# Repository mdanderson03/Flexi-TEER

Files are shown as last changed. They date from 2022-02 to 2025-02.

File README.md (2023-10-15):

# 






## What is Flexi-TEER

Flexi-TEER is an adaptable, powerful open-source transepitheal electrical resistance measurement device. Such tool is used by scientists who want to estimate the thickness of the layer of cells in a non-distructive way.

**T**rans**E**pithelial **E**lectrical **R**esistance (TEER) is an electrophysiology technique where resistance across a cell layer is measured as a proxy for ion flow which is related to inter-cellular tight junction formation.

## Where we are

At the moment the project is at the stage of hardware testing and software development. The testing status can be tracked in [this document](/Electronics/6_BringUp/FlexiTeer_BringUp_report.odt).
We recommend using OnlyOffice for the table of contents to work correctly.

Photo of the prototype

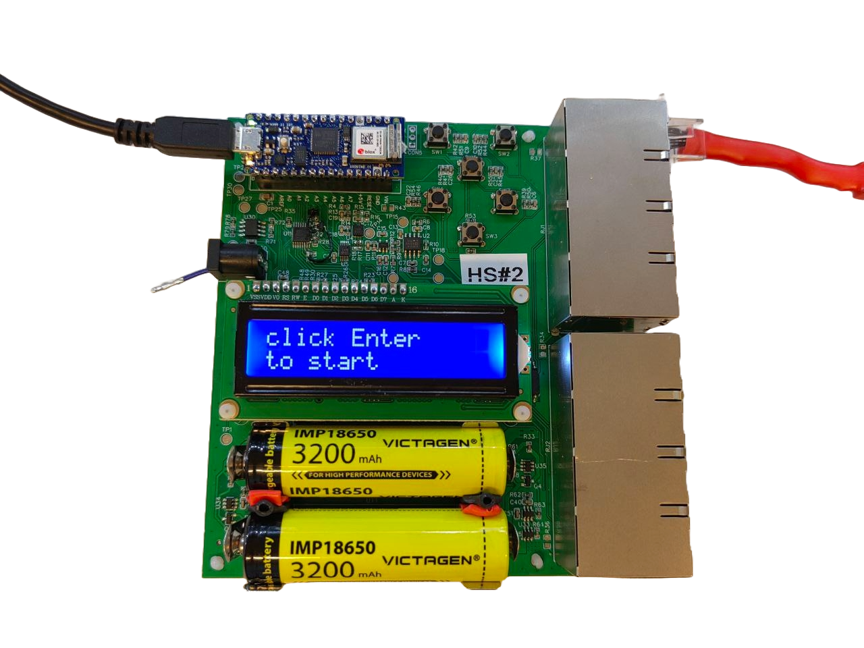
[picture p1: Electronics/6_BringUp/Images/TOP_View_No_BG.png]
TOP_View


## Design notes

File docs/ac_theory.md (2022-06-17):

# AC Theory

The DC analysis section is interesting, but not practical. The charge build up on membranes is a health hazard to the cells and it still depends on measuring within a time window. Too fast and charge has not sufficiently built
up on the cells membrane to force all of the current through the tight junctions. Too slow and and the current can become too low to accurately measure. 

To address these concerns and to extract more components, we turn to AC analysis.

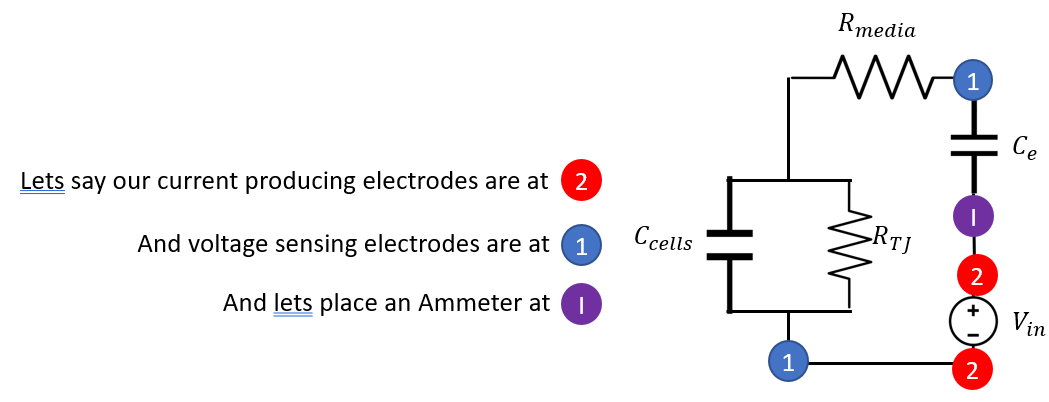
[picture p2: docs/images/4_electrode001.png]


We are still using the 4 electrode circuit, but we just use AC current instead of DC.

```math
\tag{1} Z = Z_{1}+Z_{2}
```

```math
\tag{2} Z_{1}=R_{med}+ \dfrac{-j}{\omega*C_{e}}
```

Where -j is imaginary i (standard syntax for electronics as i is typically a current value) and omega is angular freq. 

```math 
\tag{3} Z_{2}= \dfrac{1}{\dfrac{1}{R_{TJ}}+j*\omega*C_{cells}}=\dfrac{R_{TJ}}{1+j*\omega*C_{cells}*R_{TJ}}
```

Multiple (3) by the complex conjugate of its denominator

```math
Z_{2}= \dfrac{R_{TJ}*(1-j*\omega*C_{cells}*R_{TJ})}{1+\omega^2*C_{cells}^2*R_{TJ}^2}= [\dfrac{1}{1+\omega^2*C_{cells}^2*R_{TJ}^2}]*(R_{TJ}-j*\omega*C_{cells}*R_{TJ}^2)
```

Separate terms that are real and imaginary

```math
Z = [\dfrac{1}{1+\omega^2*C_{cells}^2*R_{TJ}^2}]*[(R_{TJ}+R_{med}+\omega^2*C_{cells}^2*R_{TJ}^2)+ j*[(-\omega^2*C_{e}*C_{cells}*R_{TJ}^2-1-\omega^2*C_{cells}^2*R_{TJ}^2)*\dfrac{1}{\omega*C_{e}}]]
```

Lets make some new variables to make it easier to read

```math
\tag{6} \alpha = \dfrac{1}{1+\omega^2*C_{cells}^2*R_{TJ}^2}, \quad \beta = \dfrac{1}{\omega*C_{e}}
```

Sub (6) into (5)

```math
Z = \alpha*[(R_{TJ}+R_{med}+\omega^2*C_{cells}^2*R_{TJ}^2) +j*\beta*[-\omega^2*C_{e}*C_{cells}*R_{TJ}^2-\omega^2*C_{cells}^2*R_{TJ}^2-1]]
```

Lets reduce this further

```math
R_{base}= R_{TJ}+R_{med}+\omega^2*C_{cells}^2*R_{TJ}^2, \quad and \quad X_{base} =-(\omega^2*C_{e}*C_{cells}*R_{TJ}^2+\omega^2*C_{cells}^2*R_{TJ}^2+1)
```

```math
\tag{7} Z = \alpha*[R_{base} -j*\beta*X_{base}]
```

Next to find the total resitance we must find the complex magnitude to solve for it. 

```math
\tag{8} \mid Z \mid = \sqrt[2]*{z*z^{\star}}= \alpha*\sqrt[2]*{R_{base}^2+\beta^2*X_{base}}
```

Lets look at some cases. The first will be high frequency.

```math
\tag{9} if \quad w \gg 1, \beta*X_{base} \approx \dfrac{\omega^2}{\omega*C_{e}} (C_{e}*C_{cells}*R_{TJ}^2+C_{cells}^2*R_{TJ}^2) \propto \omega
```

```math
\tag{10} R_{base} \approx \omega^2*C_{cells}^2*R_{TJ}^2*R_{media} \propto \omega^2 
```

R_base contributes to a higher degree than X_base and thus

```math
\tag{11} Z \approx \alpha*\omega^2*C_{cells}^2*R_{TJ}^2 \approx \dfrac{\omega^2*C_{cells}^2*R_{TJ}^2*R_{media}}{\omega^2*C_{cells}^2*R_{TJ}^2}=R_{media}
```

Now lets turn to the opposite end of the spectrum and find the solution at small omegas

```math
\tag{12} at \quad \omega \ll 1, \quad  X_{base} \approx 1 , \quad R_{base} \approx R_{TJ} +R_{media}
```

and

```math
\tag{13} \alpha \approx 1, \quad \beta = \dfrac{1}{\omega*C_{e}}
```

thus

```math
\tag{14} Z \approx \sqrt[2]*{(R_{TJ} +R_{media})^2 + \dfrac{1}*{\omega*C_{e}}^2} \approx \dfrac{1}{\omega*C_{e}}
```

In summary

```math
\tag{15} if \quad \color{blue}{\omega \gg 1, \quad Z \approx R_{media}} \color{black} \quad and \quad at \quad \color{red}{\omega \ll 1, \quad Z \approx \dfrac{1}{\omega*C_{e}}}
```

This allows us to perform something called impedence spectroscopy. At low freq we can determine the electrode capacitance and at high freq we can determine the resistance in the media. Subbinng those terms in and doing
a regression to the full solution allows us to determine the cell capacitance and tight junctional resistance. Notice too in this method that nothing was time depended and thus no integrals to perform over hard to determine variables.
Below is a sample spectra of impedences from the full solution.

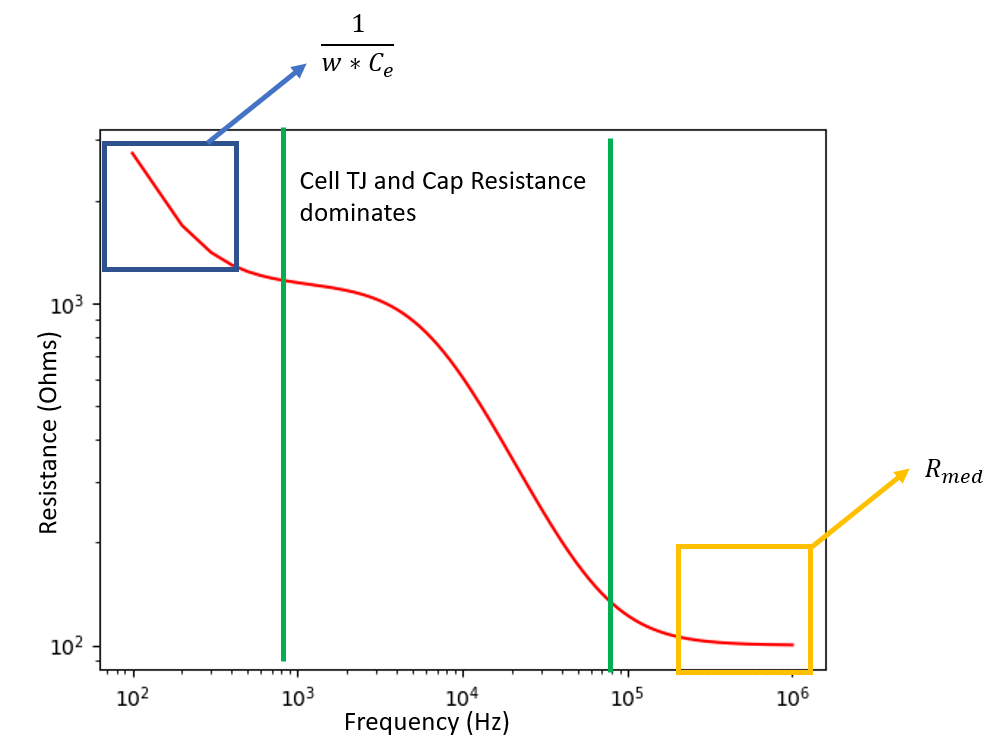
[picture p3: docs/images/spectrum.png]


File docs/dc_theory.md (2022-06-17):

# DC Theory

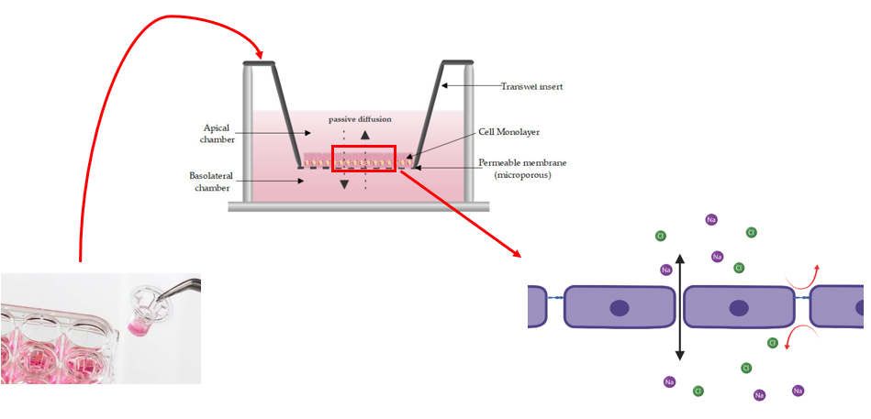
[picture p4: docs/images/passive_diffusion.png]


The typical use of TEER is with transwells. In these, monolayers of cells are formed and ions can passively diffuse through the gaps between cells.

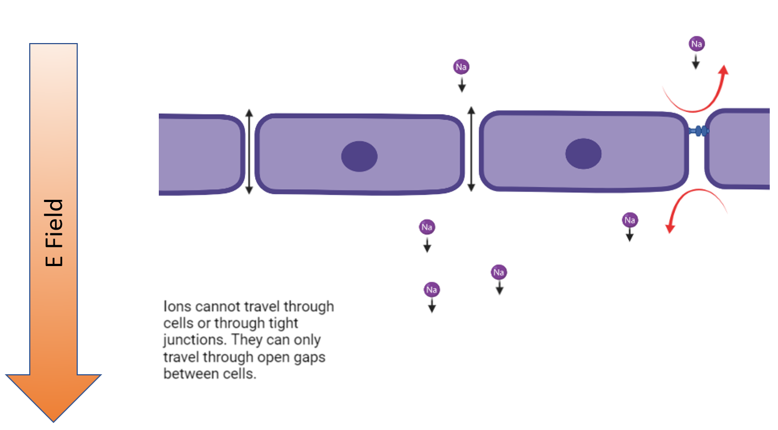
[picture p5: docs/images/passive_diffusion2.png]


Lets start forming a model on this. So if a gap has a tight junction formed, it blocks the ion from going through it. If it lacks a tight junction, then the ion can go on through. Lets translate that into a simple electrical circuit model.

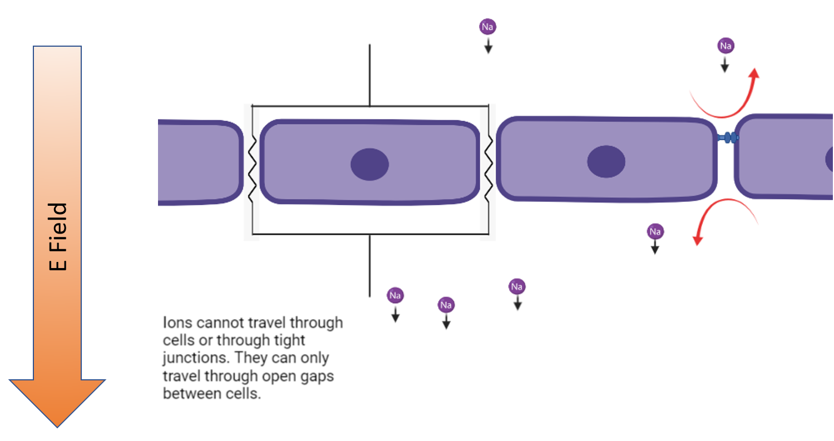
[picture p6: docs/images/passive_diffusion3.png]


So we replace tight junctions and cells with open circuits and given gaps restrict the rate that charged particles can pass through the monolayer, lets say they are  resistors. So **tight junctions and cells = open circuit** and **gaps = resistors**

**Ohm's Law**
```math
 \tag{1} V = I*R 
```

**Parallel Resistance Equivalency**
```math 
 \tag{2} R_{eq} = \dfrac{1}{(\sum{\dfrac{1}{R_g}})}
```

All gap resistances are approximately equal

```math 
  \tag{3} R_{1} \approx R_{2} \approx R_{3} \approx ... \approx R_{G}
```

Sub [3] into [2]

```math 
 \tag{4} R_{eq} = \dfrac{1}{(\dfrac{1}{R_G}*N_{G})}=\dfrac{R_{G}}{N_{G}}
```

```math 
 \tag{5} N_{CJ}=N_{TJ}+N_{G} \to N_{G} = N_{CJ}-N_{TJ}
```

Sub (3) into (4) and taylor expand 

```math 
 \tag{6} R_{eq}=\dfrac{R_{G}}{N_{CJ}*(1-\dfrac{ N_{TJ}} {N_{CJ}})} \to \dfrac{R_{eq}*N_{CJ}}{R_{G}} = \dfrac{1}{(1-\dfrac{N_{TJ}}{N_{CJ}})} \approx 1+ \dfrac{N_{TJ}}{N_{CJ}}
```

Thus

```math 
 \tag{7} R_{eq} \propto N_{TJ}
```

In the previous model we considered cell bodies themselves as open circuits, but is that accurate? Check out the image below to see that they are more accurately capacitors!

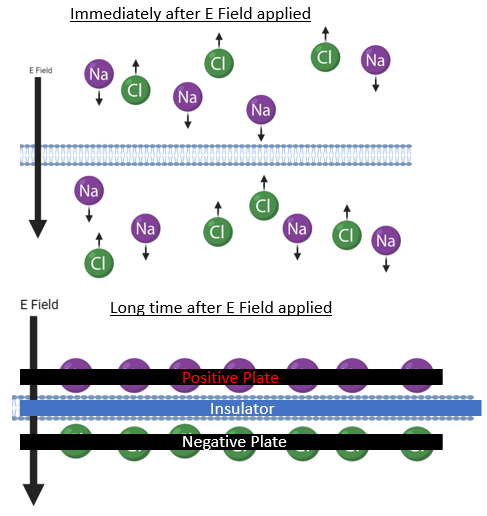
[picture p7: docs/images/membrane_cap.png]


Now lets add the cell capacitance and resistance due to the media into the model circuit

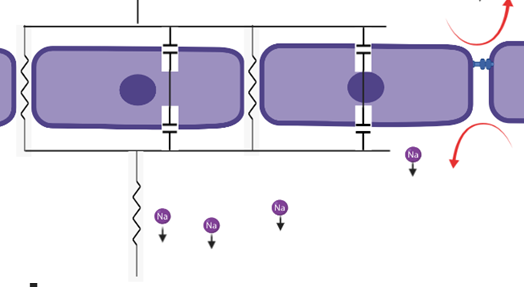
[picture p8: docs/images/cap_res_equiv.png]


We need Kirchoff Loop and Node Equations to solve this one:

```math 
 \tag{8} \color{blue}{V_{in}-R_{media}*I -R_{TJ}*I_{TJ}=0}
```

```math 
 \tag{9} \color{red}{V_{in}-R_{media}*I-V_{cells}=V_{in}-R_{media}*I-\dfrac{Q}{C_{cells}}=0}
```

```math 
 \tag{10} \color{yellow}{I=I_{TJ}+I_{cells}}
```

The node and loops look like this (color coordinated)

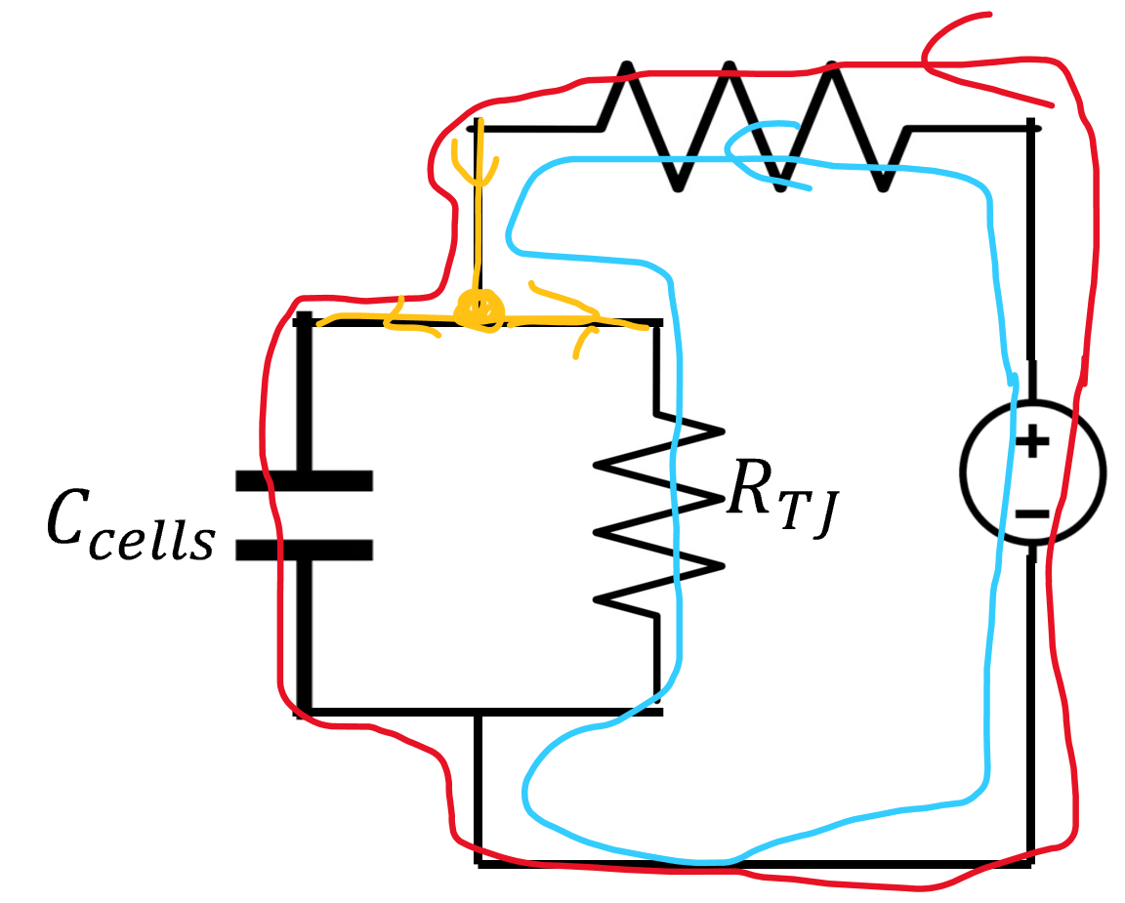
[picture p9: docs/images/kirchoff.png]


Set (8) equal to (9)

```math 
 \tag{11} \dfrac{Q}{C_{cells}}=R_{TJ}*I_{TJ}\to \color{red}{I_{TJ}=\dfrac{Q}{R_{TJ}*C_{cells}}}
```

Sub (11) into (10)

```math 
 \tag{12} I = \dfrac{Q}{R_{TJ}*C_{cells}} + I_{cells}
```

Sub (12) into (9)

```math 
 \tag{13} V_{in}-R_{media}*(\dfrac{Q}{R_{TJ}*C_{cells}}+I_{cells})-\dfrac{Q}{C_{cells}}=0
```

Divide by R media

```math 
 \tag{14} \dfrac{V_{in}}{R_{media}}-I_{cells}-(\dfrac{1}{R_{TJ}*C_{cells}}-\dfrac{1}{R_{media}*C_{cells}})*Q=0
```

Place I and Q onto opposite sides of equation

```math 
 \tag{14} -R_{media}*C_{cells}*I_{cells}=(\dfrac{R_{media}}{R_{TJ}}+1)*Q-C_{cells}*V_{in}
```

Given Q is built up on the membranes, the whole current that passes through cells is the time derivative of the charge and lets group some constants into a new constant

```math 
 \tag{16} I_{cells}=\dfrac{\delta{Q}}{\delta{t}}, \alpha = \dfrac{R_{media}}{R_{TJ}} + 1
```

Sub (16) into (15)

```math 
 \tag{17} -R_{media}*C_{cells}*\dfrac{\delta{Q}}{\delta{t}}=\alpha*Q-C_{cells}*V_{in}
```

Separate Q and t terms to opposite sides of equation

```math 
 \tag{18} \dfrac{\delta{Q}}{Q-\dfrac{V_{in}*C_{cells}}{\alpha}}=\dfrac{-\alpha}{C_{cells}*R_{media}}*\delta{t}
```

Integrate (18)

```math 
 \tag{19} \int_{0}^{Q}  \dfrac{1}{Q-\dfrac{V_{in}*C_{cells}}{\alpha}}\delta{Q}=\int_{0}^{t} \dfrac{-\alpha}{C_{cells}*R_{media}}\delta{t}
```

Solution to (19)
```math 
 \tag{20} \ln{\dfrac{Q-\dfrac{V_{in}*C_{cells}}{\alpha}}{\dfrac{-V_{in}*C_{cells}}{\alpha}}}=\dfrac{-\alpha*t}{C_{cells}*R_{media}}
```

Raise each side to power e and solve for Q

```math 
 \tag{21} \color{red} Q(t)=\dfrac{V_{in}*C_{cells}}{\alpha}*(1-e^{\dfrac{-\alpha*t}{C_{cells}*R_{media}}})
```

now lets solve for I and V for cells (time derivative of Q and Q/C respectively)

```math 
 \tag{22} \color{red} I_{cells}(t)=\dfrac{V_{in}}{R_{media}}*e^{\dfrac{-\alpha*t}{C_{cells}*R_{media}}}
```
```math 
 \tag{23}  \color{red} V_{cells}(t)= \dfrac{V_{in}}{\alpha}*(1-e^{\dfrac{-\alpha*t}{C_{cells}*R_{media}}})
```

Now lets insert a volt and an am meter into the circuit

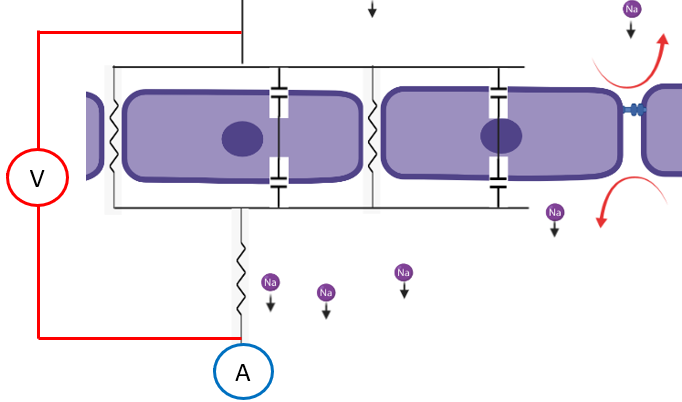
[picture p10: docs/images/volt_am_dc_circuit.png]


```math 
 \tag{24} V_{meter}(t)=R_{TJ}*I_{TJ}(t)+R_{media}*I(t)
```

```math 
 \tag{25} Blank = R_{media}*I(t)
```
```math 
 \tag{26} V_{meter}(t)-Blank=R_{TJ}*I_{TJ}(t)
```

```math 
 \tag{27} I_{meter}(t)=I(t)=I_{cells}+I_{TJ} \to I_{TJ}=I_{meter}(t)-I_{cells}
```

Sub (22) into (27)

```math 
 \tag{28} I_{TJ}(t)=I_{meter}(t)-\dfrac{V_{in}}{R_{media}}*e^{\dfrac{-\alpha*t}{C_{cells}*R_{media}}}
```

Sub (28) into (26) and solve for the tight junctional resistance

```math 
 \tag{29} \color{red}R_{TJ}=\dfrac{V_{meter}(t)-Blank}{I_{meter}(t)-\dfrac{V_{in}}{R_{media}}*e^{\dfrac{-\alpha*t}{C_{cells}*R_{media}}}}
```

So to solve for tight junctional resistance we must know how current has been applied to the circuit. That is a finicky to determine and beyond this we have a confounding factor of tight junction resistance being in the alpha term. To rectify this, lets drive this to inifinite time

```math 
 \tag{30} R_{TJ}(t)=\dfrac{V_{meter}(t)-Blank}{I_{meter}(t)}
```

This equation is easily solved with our instruments as long as we wait long enough. Lets take a stab at how fast that might be given I dont have infinite time to wait. Lets say we want to wait until the cell current has fallen to a factor of 0.01% of its original value

```math 
 \tag{31} 0.0001 =e^{\dfrac{-\alpha*t}{C_{cells}*R_{media}}}
```

```math 
 \tag{32} \ln{0.0001}=\dfrac{-\alpha*t}{C_{cells}*R_{media}}, \alpha \approx 1 \quad if \quad R_{TJ} \gg R_{media}
```

```math 
 \tag{33} -R_{media}*C_{cells}*\ln{0.0001}=t
```

To find cells we take the unit capacitance and multiply by transwell area

```math 
 \tag{34} C_{cells}=A_{transwell}*C_{unit}=3.3*10^{-5}*1*10^{-2}=3.3*10^{-7}, R_{media} \approx 50
```

```math 
 \tag{35} t = 3.3*10^{-7}*50*\ln{0.0001} \approx 0.1ms 
```

So saturation occurs very rapidly! We have another issue now. Its something that wasn't addressed in the previous model. Lets check out what happens to an electrode the second current flows from it. 

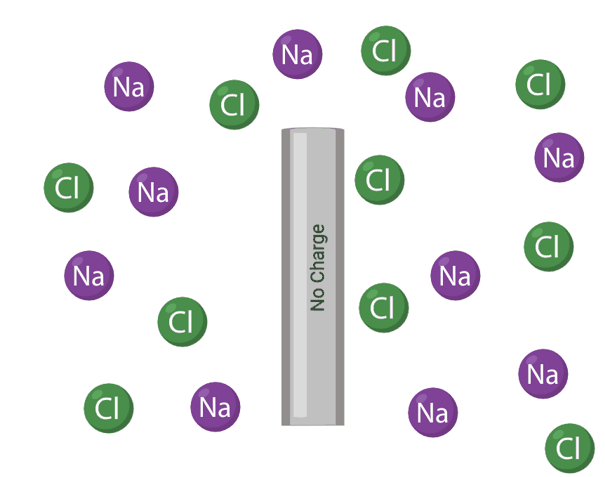
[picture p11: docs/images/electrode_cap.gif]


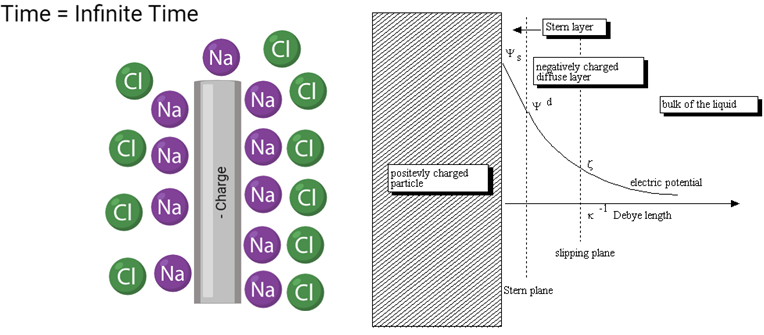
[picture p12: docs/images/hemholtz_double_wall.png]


  As can be seen, a double wall is created whenever an electrode generates current in a liquid with negative and positive ions in it. This creates another component called electrode capacitance that we must add into the circuit. Beyond this, thus far we have neglected to consider a trans-cellular transport component. Here is the new circuit.

.. image:: C:\Users/mike/Documents/GitHub/Felxi-TEER/images/teer_theory/el_cap_trans.png
  :width: 800

```math 
 \tag{36} R_{TJ}+R_{TC}=R_{cells}
```

Experiments can be made to emphasize the transcellular transport component, but in general

```math 
 \tag{37} R_{TJ} \gg R_{TC}
```

```math 
 \tag{38} R_{cells} \approx R_{TJ}
```

Instead of resolving the entire equation with electrode capacitence in it, lets think of them like a current squeeze. At t=0, its like a short circuit, at infinite time its like a closed circuit. We also know the general form of how the current will change over time. 

```math 
 \tag{39} R_{TJ}=\dfrac{V_{meter}(t)-Blank}{I_{meter}(t)-\dfrac{V_{in}}{R_{media}}*e^{\dfrac{-\alpha*t}{C_{cells}*R_{media}}}}* \color{red} \dfrac{1}{e^{\dfrac{-\beta*t}{C_{e}*R_{media}*R_{TJ}}}}
```

I dont really care what beta actually is. This is the correct form and that is all that is needed for this approximation. Lets see where this equation goes as t goes to infinity

```math 
 \tag{40} as \quad t \to \infty, \quad R_{TJ} \to \infty
```

This is nonsense, right? tight junctional resistance is constant, but what happened? In this model we assumed that all voltage dropped occured over media and the tight junctions. Now we are getting a drop over the electrode capcitance too. Lets substract that from (39) to get the proper equation.

```math 
 \tag{41} R_{TJ}=\dfrac{V_{meter}(t)-Blank- \color{red} V_{c}(t)}{I_{meter}(t)-\dfrac{V_{in}}{R_{media}}*e^{\dfrac{-\alpha*t}{C_{cells}*R_{media}}}}*\dfrac{1}{e^{\dfrac{-\beta*t}{C_{e}*R_{media}*R_{TJ}}}}
```

We have an issue though. The voltage drop over the electrode capacitance depends on time so we would need to solve the equation

```math 
 \tag{42} \int_{0}^{t}I_{electrode}dt = \int_{0}^{t}\dfrac{1}{e^{\dfrac{-\beta*t}{C_{e}*R_{media}*R_{TJ}}}}dt
```

That equation is difficult to solve accurately since it depends on us again knowing the exact time since the circuit was turned on. Is there a way to bypass this component though?



Up until now I was using the same electrodes to generate the current and read the voltage. If we make a new configuration where 2 separate voltage sensing electrodes are added and placed between the current electrodes and cell sample, we get a new configuration where the part of the circuit that the electrodes are measuring does not inlcude the electrode capcitor component, thus making it so we can revert make the original equation that never depended on the voltage drop over the electrode capacitor. Thus

```math 
 \tag{43} \color{red} R_{TJ}=\dfrac{V_{meter}(t)}{I_{meter}(t)} - R_{blank}
```

This still has a caveat where the electrode capacitance is still pinching current off. While my tight junctional resistance value does not care, at some point my current will become so small that my electronics cannot accurately measure it anymore. Now you may be asking well current still must go into the voltage electrodes right? In that case won't they get capacitence themselves and we will be back in the same same boat. This is true and capacitance is a geometrical term so our capacitence is the same (assuming the electrodes are identical in shapes), but there is one big thing here. 

```math 
 \tag{44} V=\dfrac{Q}{C}
```

The voltage drop is what really matters when we are measuring voltage differences, not the capcitence itself. If infinite time elapses we will be in the same boat, but in shorter time frames we are good. This is due to the current that the voltage electrodes flow is in the order of picoamps while the current electrodes make micro amps. This means the voltage drop over the voltage electrodes capacitence is much much lower at short time frames since the charge can only accumulate at a very low rate.

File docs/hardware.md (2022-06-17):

# Hardware

!The basic goal of this electronic device is to create a low fixed current, AC square wave with modulatable frequency and measure the voltage difference between the current electrodes. 

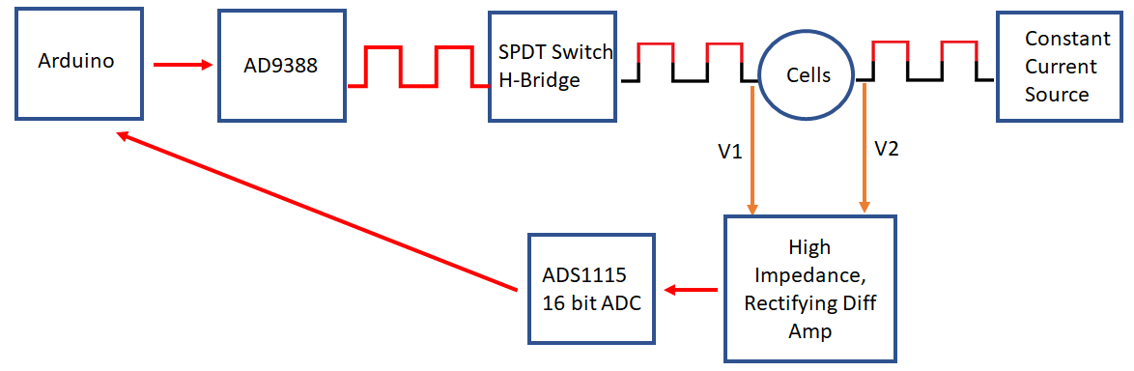
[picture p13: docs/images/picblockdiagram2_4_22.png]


Looking at the block diagram we can see that An Arduino was used as the microcontroller for the device. A AD9388 breakout board generates a square wave timing wave that goes between V and 0 volts. An H-Bridge made from single throw dual throw (SPDT) switches allows it to be made into an AC wave at the same freq, but between +-V Volts. A constant current chip forces the current in that AC wave to be locked into a small value (20uA). The voltage difference over the cells then goes into a high input impedance diff amp. Since the incoming signal is +-V_diff, it would generate an AC output which is then hard to read off. So inside that block are two more SPDT switches to flip what input what end goes to so that the high V is always in the same input which effectively makes the diff amp output a DC signal. This signal then goes into a 16bit ADC which can be read off onto the Arduino. 

All schematics and PCB design we performed on the EasyEDA website. Click here to be directed to the project on [EasyEDA](https://oshwlab.com/md.anderson03/flexi-teer)

Lets take a look at and explore the overall schematic:



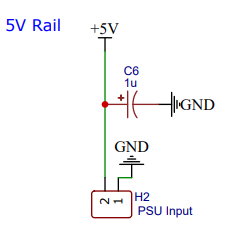
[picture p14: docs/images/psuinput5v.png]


Primary power supply is a 5V external supply which is filter by internal 1uF cap. 

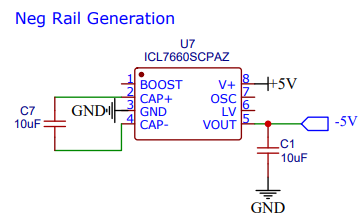
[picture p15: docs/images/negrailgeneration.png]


Use switching regulator chip to generate negative voltage rail which is needed for OP Amps in circuit to function properly. 

>!! **Warning**
>!! This part has been an issue. Gets very hot and tends to fail rapidly.

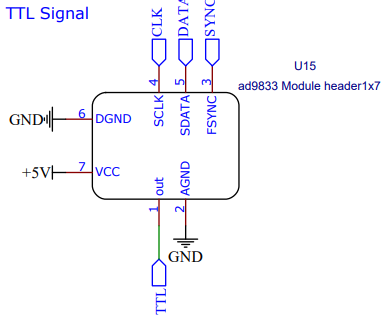
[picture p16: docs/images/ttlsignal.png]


The AD9388 chip is the effective "clock" for this device. It has a serial connection to the Arduino and can modulate its square wave output freq between single hertz and mega hertz. This provides the Arduino with a signal that triggers it to ask for a voltage read with (some delay/phase shift may be added to that in the Arduino itself). It also flips the output of all 6 SPDT switches. This allows them to generate an AC square wave allows them to flip polarity on the differential amp so that its output is DC like and positive. 

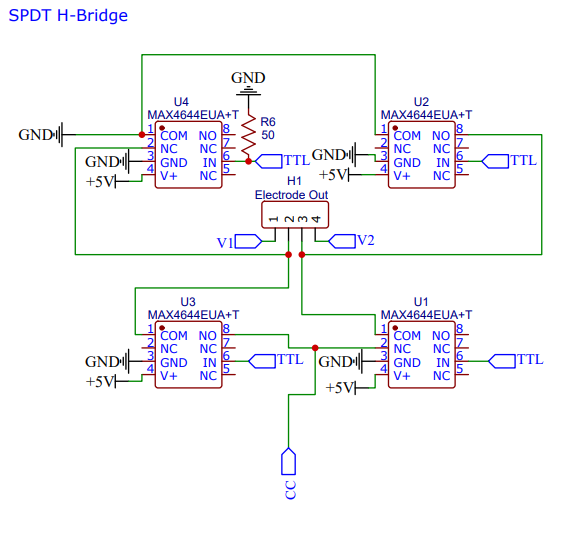
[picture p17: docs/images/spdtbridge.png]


This section converts the incoming TTL wave into an AC version. Its the exact same construction as a DC motor H-Bridge, but instead of bi-junctional transistors, it uses SPDT switches. This allows it to perform at MHz and have minimal artifacts. 

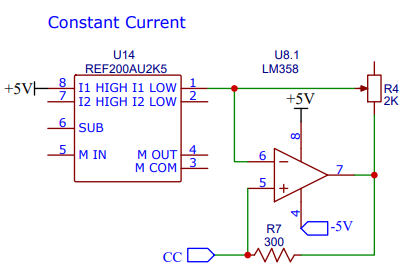
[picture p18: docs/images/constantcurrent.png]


This module needs a constant current source. The REFE200AU2K5 IC has a built in 100uA constant current source. The goal for this device was 20uA. To accomplish that a LM358 op amp was added to scale down the current. A potentiometer is installed which allows this current to be modulated. 

>i **Note**
>i The potentiometer is not ideal. Future versions could replace the pot with something digitally controlled to auto calibrate itself. 

**Voltage Signal Processing**

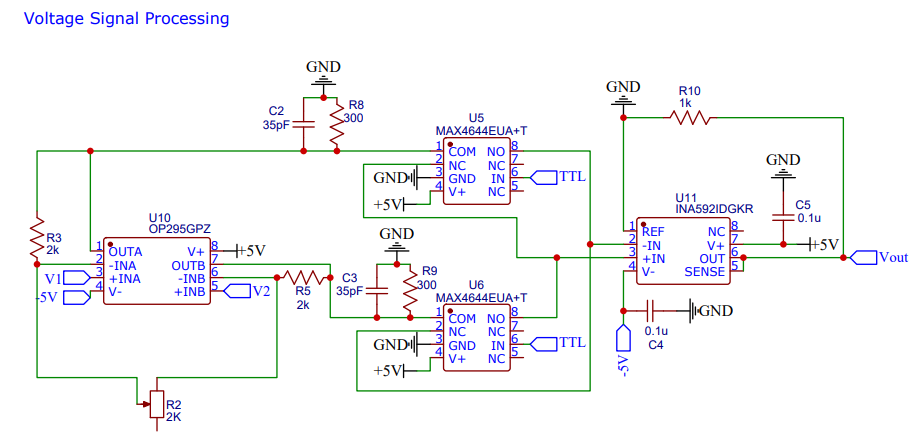
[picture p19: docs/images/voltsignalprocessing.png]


This uses a high impedance instrument amp. This means dual op amps interface directly with the V1 and V2 electrodes from the H-Bridge. The ultra high impedance of op amps means extremely little current is taken from the H-Bridge itself (essentially sample without disturbing the system) and then 2 SPDT switches can flip as needed to make sure the higher V value is on the V+ input of the difference amp. This way the output signal from it is effectively the absolute value of V1-V2 which is a psuedo DC signal. 

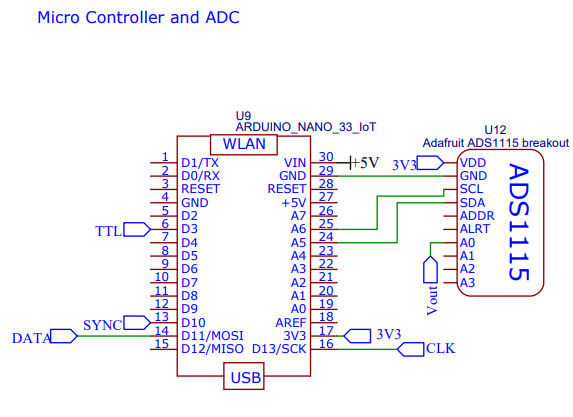
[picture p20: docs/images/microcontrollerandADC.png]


We employed an Arduino Nano 33 IoT as the microcontroller. This was chosen as it gives the ability to connect to wifi. The ADS1115 16 bit ADC is able to read off the voltage that comes from the voltage signal processing circuit module.

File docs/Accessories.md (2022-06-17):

# Accessories
This catagory encompasses all things outside of electronics for the Flexi-TEER device. The primary device accessories desired are:

1. Currently, models for a cell that holds transwells and electrodes in place and a platform that holds 12 of these cells are created in tinkercad. This is not a good platform and both of these need recreated in FreeCAD. If you contact me, I will give you access to the tinkercad account which will allow you to get the information needed to recreate it.  

* Case for electronics. The initial goal is to create a case that has a LCD screen and a RJ45 jack for the electrode in it. Inspiration can be taken from the World Instrumentation's EVOM meter. 

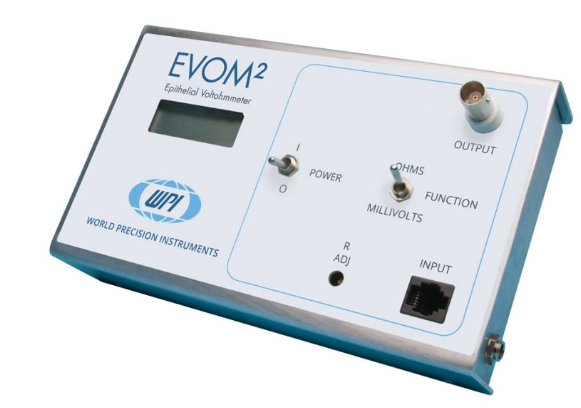
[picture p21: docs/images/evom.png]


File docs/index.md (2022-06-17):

#Flexi-TEER



Welcome to the Flexi-TEER project. This project is about an adaptable, powerful open-source transepitheal electrical resistance device. 

At this moment, we are looking for new people to contribute to this open source project. Please check the modules that need development page to see what areas you can contribute in. 

* [Assembly Instructions](assembly_instructions.md)
* [General Use.](General_use.md)
* [Tutorials](Tutorials.md)
* [Theory](theory.md)
* [Needed Modules](needed_modules.md)
* [Contribution Guide](contribution_guide.md)

 The following link is for the [bill of materials]{BOM} page.

## What is TEER

**T**rans**E**pithelial **E**lectrical **R**esistance (TEER) is an electrophysiology technique where resistance across a cell layer is measured as a proxy for ion flow which is related to inter-cellular tight junction formation. 

## Why Do We Need an Open-Source TEER Device?
Currently, the primary commercial product is the [EVOM meter](https://www.wpiinc.com/evom3-epithelial-volt-ohm-teer-meter-3) from World Instrumentation. This device is not cheap, but also not super expensive. The real downside is that it lacks flexibility and connectivity. Examples of these are wireless communication with device via a python based API and reading sequentially through multiple electrodes. 

On the open-source side, no good solution currently exists. Current attempts are listed below:

* [EVOM Add on](https://www.ncbi.nlm.nih.gov/pmc/articles/PMC8000980/)
* [Low Cost TEER](https://chemrxiv.org/engage/chemrxiv/article-details/60c746bdbb8c1aa1073da918)
* [Simple Meter](https://www.jove.com/v/60087/a-simple-approach-to-perform-teer-measurements-using-self-made-volt)

Going through these options depend on the proprietary EVOM meter as a base, are dangerous and inaccurate or are clunky via the use of signal generators and multimeters. None of these are sufficient platforms to build off of. 

## Project Goals

#### Device Goals
1. Robust TEER measurement operation (Fixed Frequency and Frequency Sweep)
* WiFi interface with a Python API

#### Accessory Goals
1. 3D printed cell to hold transwell inserts and keep electrodes in position
* 3D printed platform to hold series of above cells.

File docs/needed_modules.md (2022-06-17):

# Modules that need development

Below is an overview of areas where we need contributors in. If you are interested in contributing to this project, please read through the **[Contribution Guide](contribution_guide.md)** beforehand. 
## [Hardware](hardware.md){step}
* Parts to be added
    * Multiplex IC
    * Self Calibration Capability
    * RJ45 Input Jack for Electrode</ul>
**Current Schematic Below**:



## Hardware Testing
All hardware has been breadboard tested, but further testing and characterization with multimeters and oscilloscopes are needed. 

## [Accessories](Accessories.md){step}

We need the models below recreated in FreeCAD and a case for the electronics created. 

* TEER chamber that holds transwell in place as well as electrodes. Below is current model. 



* Device to hold a series of these transwell cells in place. 



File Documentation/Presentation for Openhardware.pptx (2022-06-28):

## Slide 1

Dr. Michael Anderson
Staff Scientist
Boston Children’s Hospital
Boston, Massachusetts, United States

## What is Transepithelial Electrical Resistance (TEER)?

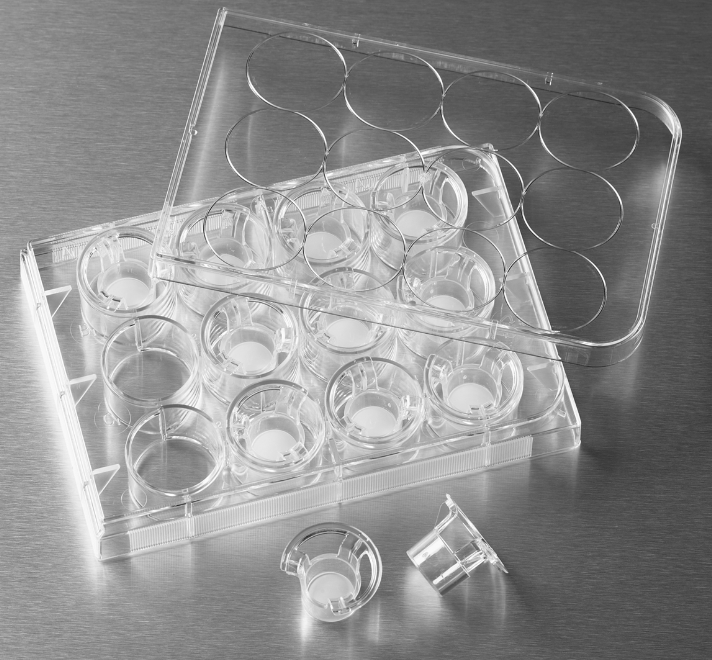
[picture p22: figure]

Equivalent circuit diagram

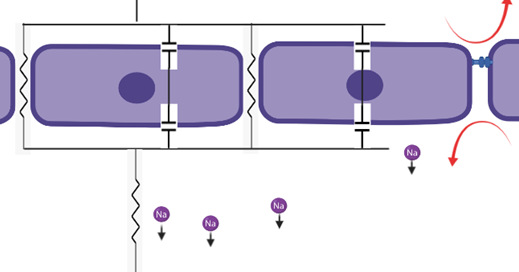
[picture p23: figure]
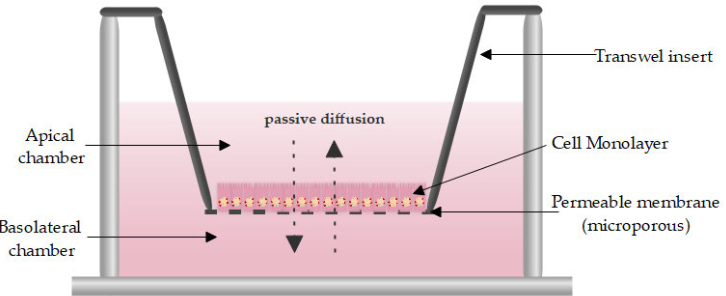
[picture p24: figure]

Essentially, TEER measures resistance of ion movement through cells and cell gaps

## Where is it used?

Common Usage

- Mostly epithelial barrier research labs
- Most common platform are transwell inserts
- Used to monitor tight junctional formation in transwell polarized monolayers

- Ion flux through cell-cell gaps as a function of time, drug additions, genetic manipulations
- Pairing electrophysiology with microscopy and microfluidics
- Adapt to different biological models
- Modify to explore more electrophysiology phenomena

Potential Future Usage

## What is Currently Available?

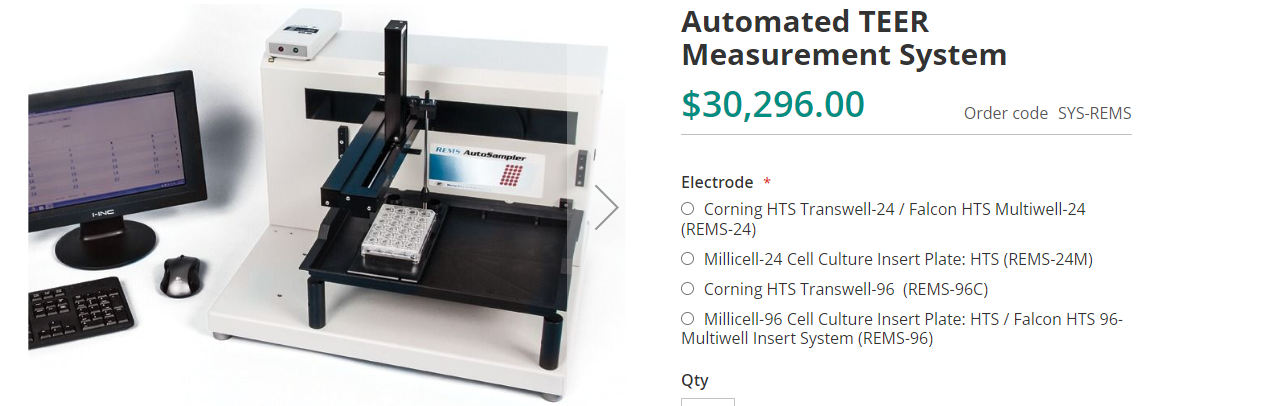
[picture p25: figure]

- World instrumentation is the commercial leader with TEER devices
- EVOM 2 and 3 meters are affordable, but extremely limited in capabilities
- Automated system is much more repeatable and automated, but still restrictive with platform choice and no incubation and is expensive
- No sufficient open-source alternative exists


## Flexi-TEER Goals

1. Flexible. Basic unit can attach to almost any electrode-based device, and both generate the needed current and read off resulting voltage
2. Modulatable. Alter any relevant parameters of device from frequency, peak amplitude, duty-cycle, read frequency, etc.
3. Reliable. All electrical characteristics are documented. No one wants to use something if they cant trust it
4. Affordable. Greatly expand what labs are able to leverage TEER devices to achieve new experiments and build more repeatable cell model system.

## Current Status of Project and needs

- Theory derived
- Basic schematic is finished, and PCB designed

Needed Contributions
1. Electrical Engineering. I am a physicist and I need someone who understands practical implementation of electronics and refined PCB design
2. Accessory Design. We need accessories to use the device with. Examples are casing for PCB, incubation chamber to hold transwell inserts, reliably place electrodes and be sterilizable.
3. Electrode Design
4. Testing and Documentation. Building good guides and documentation and testing made equipment


## What is in it for me and how to contact

1. Contribute to meaningful research and advancement of research into new areas
2. Have impact on research direction (how device is applied)
3. It is interesting!
4. Become a coauthor on papers pertaining to device

Contact

- Email Michael Anderson at Michael.Anderson@childrens.Harvard.edu
- Don’t need predefined role or ideas to join. We can discuss your role based on your interests and skill set

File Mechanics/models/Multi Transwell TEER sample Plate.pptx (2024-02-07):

## Multi Transwell TEER sample Plate

## Constraints

1. Hold 12 transwells
2. Easily organized wiring that is hardish to damage
3. Autoclavable and reusable
4. Interface with multiplexing flexi-teer unit
5. Repeatable and stable positioning of electrodes

## Approach

1. To interface with flexi-teer in an easy and organized fashion, I will build in on board PCBs. Wires from electrodes will solder into them and funnel into multiwire receptacles. These receptacles will then connect to just a couple cables to link to the flexi-teer unit
2. To be autoclavable, device will be SLA 3D printed with autoclavable dental resin: https://www.liqcreate.com/product/bio-med-clear-biocompatible-resin/ In addition, the PCB will be completely coated in a potting epoxy and will use 24+ wire autoclave compatible receptacles from fisher connection.
3. To be compact, the device will be broke into two parts. The basin and the lid. The basin will look very similar to a multiwell plate, but with the configuration of a 6x2 well pattern. The lid will attach magnetically to the basin and will be flat with no rim. This will create a stable but still removable lid.
4. Electrodes will be about 18gauge silver wire and permanently affixed into drilled sockets in both the lid and basin portions.

## Course Model (Side View)

Magnet

Electrodes

Lid

Transwell

Basin

Magnet

Electrodes

## Course Model (Top View)

Wires

PCB

PCB

Receptacle

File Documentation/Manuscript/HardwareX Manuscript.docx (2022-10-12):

HardwareX article template Version 2 (June 2021)

Before you complete this template, a few important points to note:

- Unsure whether your designs would make a suitable hardware article? Visit our webpage Everything you need to know about HardwareX (https://www.journals.elsevier.com/hardwarex/submit-your-hardware/everything-you-need-to-know-about-hardwarex).
- The format of a hardware article is very different to a traditional research article. To help you write yours, we have created this template. We will only consider hardware articles submitted using this template.
- HardwareX is dedicated to the communication of advances in open source scientific infrastructure. By submitting to the journal, you are confirming that all the information necessary to reproduce your design/hardware is communicated in full and is accessible for use under an open source license.
- It is important that the designs referred to in your HardwareX article are publicly available. You’ll find information on our hardware sharing criteria in the template. Not sure how to prepare your hardware for sharing? The Open Source Hardware Association (https://www.oshwa.org/sharing-best-practices/) has some best practice tips.
- Please consult the HardwareX Guide for Authors (https://www.elsevier.com/journals/hardwarex/2468-0672/guide-for-authors) when preparing your manuscript; it highlights mandatory requirements and is packed with useful advice. We have also developed a step-by-step video guide (https://www.journals.elsevier.com/hardwarex/submit-your-hardware/how-to-submit-your-scientific-hardware-article-to-hardwarex) to help you complete this template accurately and increase your chances of acceptance.

Still got questions?

- Visit our Everything you need to know about HardwareX (https://www.journals.elsevier.com/hardwarex/submit-your-hardware/everything-you-need-to-know-about-hardwarex) webpage or email us at hardwareX@elsevier.com

Now you are ready to fill in the template below. As you complete each section, please carefully read the associated instructions. All sections are mandatory.

Once you have completed the template, delete this line and everything above it before submitting your article. In addition, please delete the instructions in the template (the text written in italics).

Article title

Flexi-TEER, a wireless, multiplexing and computer automated trans-epithelial electrical resistance device.

Authors

Michael Anderson

Dennis Yaskevich

Jose Yeste Lozano

Jay Thiagarajah*

Affiliations

BCH

BWH

Wherever Dennis is

Corresponding author’s email address and Twitter handle

Jay.thiagarajah@childrens.harvard.edu

Abstract

Max. 200 words. Remember that the abstract is what readers see first in electronic abstracting & indexing services - make it brief, specific, interesting and easy to understand. If a research article refers to your hardware, cite that research article here.

Trans-epithelial electrical resistance (TEER) measurements are typically used to quantify the degree of tight junction formation in cell monolayers. This can be used a reference point to determine when transwell monolayers are ready to be used for an experiment or can be used directly in experiments that modulate tight junctions or transcellular transport. We present here for the first time, a low-cost and accurate TEER measurement device that is capable of completely replicating the industry standard WPI’s EVOM meter and expands on its capabilities with wireless computer automation and the ability to multiplex up to 15 electrodes sequentially.

Keywords

- Open source hardware
- TEER
- 3D printing
- DIY

Specifications table

Please replace the italicized instructions in the right column of the table with the relevant information about your hardware.

Hardware name | The name of the hardware that you have invented/customized
Subject area | Please select the subject area that best reflects the community for which your hardware was developed (deleting the rest): - Engineering and materials science - Chemistry and biochemistry - Medical (e.g., pharmaceutical science) - Neuroscience - Biological sciences (e.g., microbiology and biochemistry) - Environmental, planetary and agricultural sciences - Educational tools and open source alternatives to existing infrastructure - General
Hardware type | Please select the category that best reflects the purpose for which your hardware was developed (deleting the rest): - Imaging tools - Measuring physical properties and in-lab sensors - Biological sample handling and preparation - Field measurements and sensors - Electrical engineering and computer science - Mechanical engineering and materials science - Other [please specify]
Closest commercial analog | Please specify the closest commercial analog to your submitted hardware. In other words, what would this hardware replace? If no commercial analog exists, state “No commercial analog is available.”
Open source license | All designs must be submitted under an open source license (for more details see the Guide for Authors (https://www.elsevier.com/journals/hardwarex/2468-0672/guide-for-authors)). Please specify the open source license you’ve selected here.
Cost of hardware | Insert an approximate cost only - we will ask you for a complete breakdown of costs in a later section (Bill of materials).
Source file repository | If you’ve uploaded your source files to an approved repository (OSF (https://osf.io/wgk7q/wiki/home/), Mendeley Data (https://data.mendeley.com) or Zenodo (https://doi.org/10.5281/zenodo.3356702)) write the DOI URL here. For example: http://doi.org/10.17605/OSF.IO/WGK7Q
OSHWA certification UID (OPTIONAL) | We encourage you to apply for a free OSHWA Certification (https://certification.oshwa.org/), which confirms your work is open-source compliant. If certification has been acquired, insert the OSHWA UID here. For example: “CH000005”. In your OSHWA certification project description, include a link to your HardwareX publication and the tag #HX. If you haven’t acquired certification, please delete this row of the specifications table.

Hardware name | Flexi-TEER
Subject area | Please select the subject area that best reflects the community for which your hardware was developed (deleting the rest): - Electrical engineering and materials science - Medical (e.g., pharmaceutical science) - Neuroscience - Biological sciences (e.g., microbiology and biochemistry) - Educational tools and open source alternatives to existing infrastructure
Hardware type | Please select the category that best reflects the purpose for which your hardware was developed (deleting the rest): - Measuring physical properties and in-lab sensors - Biological sample handling and preparation
Closest commercial analog | World Precision Instrumentation EVOM
Open source license | All designs must be submitted under an open source license (for more details see the Guide for Authors (https://www.elsevier.com/journals/hardwarex/2468-0672/guide-for-authors)). Please specify the open source license you’ve selected here.
Cost of hardware | $150
Source file repository | If you’ve uploaded your source files to an approved repository (OSF (https://osf.io/wgk7q/wiki/home/), Mendeley Data (https://data.mendeley.com) or Zenodo (https://doi.org/10.5281/zenodo.3356702)) write the DOI URL here. For example: http://doi.org/10.17605/OSF.IO/WGK7Q
OSHWA certification UID (OPTIONAL) | We encourage you to apply for a free OSHWA Certification (https://certification.oshwa.org/), which confirms your work is open-source compliant. If certification has been acquired, insert the OSHWA UID here. For example: “CH000005”. In your OSHWA certification project description, include a link to your HardwareX publication and the tag #HX. If you haven’t acquired certification, please delete this row of the specifications table.

1. Hardware in context

Write a short description of the hardware and provide context, i.e., describe similar open hardware and proprietary equipment in the field.

Trans-epithelial electrical resistance (TEER) measurements are typically used as a proxy for degree of tight junctional formation in cell monolayer samples (ref). Normally, TEER is used to monitor the maturation of trans-well monolayer models, but it has demonstrated usages as an experimental metric in microfluidic devices as well. The standard in monitoring the maturation of cell monolayers is WPI’s EVOM meter. It is a manual device that requires the user to dunk special electrode chopsticks into each trans-well sample and manually record the resulting resistance value. Current attempts to create an open-source equivalent device of the EVOM have proven to have serious design flaws or to be unpractical (ref).

To make TEER measurements useful for experimental metrics, it needs to be computer automated. Preferably, it would be able handle many samples as well to accommodate different experimental conditions and replicates. While the EVOM unit itself is incapable of those features, an open-source add on device exists for the EVOM that allows it to be computer automated and to handle 4 samples at a time (ref). Ultimately, this is only a half measure that is still limited in the number of samples it can measure and relies on expensive proprietary equipment.

Here we present a new open-source built from the ground up TEER device that is low-cost, easy to build and does not rely on any proprietary equipment. It is capable of wireless computer automation for both triggering and recording and to handle up to 15 samples at a time. In addition, all parameters involved such as constant current, frequency and sampling time points can be altered. Construction is done via PCB manufacturing and pick and place component soldering alongside a 3D printable case. Great effort was given to making sure that the component selected were widely available and affordable.

2. Hardware description

Describe your hardware, highlighting the customization rather than the steps involved in the procedure. Explain how it differs from other hardware and the advantages it offers over pre-existing methods. For example, how does this hardware compare to other hardware in terms of cost or ease of use, or how can it be used to develop further designs in a particular area?

Add 3-5 bullet points which broadly explain to other researchers - inside or outside of the original user community - how the hardware could help them, with either standard or novel laboratory tasks.

Flexi-TEER is a fully contained TEER measurement device. It is possible to use it in the exact same manner as the EVOM meter is or use it in a more expanded manner with multiplexing and computer automation. If used as an EVOM alternative, we have a specific 3D printed case that allows it to look similar to it and has a built in LCD screen and on-board battery.

Design files

Your design files should be editable - see OSHWA’s open source definition of ‘Documentation’ (https://www.oshwa.org/definition/) for further details. You must then either:

- Upload your design files to one of the three approved online repositories - Mendeley Data (https://data.mendeley.com/) (instructions (https://doi.org/10.5281/zenodo.3346799)), the Open Science Framework (https://osf.io/) (instructions (https://osf.io/wgk7q/wiki/home/)) or Zenodo (https://zenodo.org) (instructions (https://doi.org/10.5281/zenodo.3346799)). We recommend this option as the repositories support versioning of files.
- Upload your design files as supplementary materials (e.g., CAD files, videos…) to Hardware X’s online editorial system when you submit your manuscript.
- Include your design files in the body of the manuscript (e.g., as figures).

CAD files: You are encouraged to use free and open source software packages for creating the files. For CAD files, OpenSCAD (http://www.openscad.org/), FreeCAD (http://www.freecadweb.org/), or Blender (https://www.blender.org/)are encouraged, but, if these are not available, we accept source files from proprietary CAD packages, such as Autocad or Solidworks, and other drawing packages.

3D printing. Supplementary files that facilitate digital replication of the devices are encouraged; for example, STL files for 3D printing components. We recommend uploading CAD files to the NIH 3D Print Exchange (http://3dprint.nih.gov/) as Custom Labware and then entering the link here.

Electronics: PCB layouts and other electronics design files can be uploaded to the Open Hardware Repository (http://www.ohwr.org/) or other repositories or as supplementary materials.

Software and firmware: All software files used in the design and operation of the hardware should be included in the repository. Provide a description of the software and firmware and use extensive comments in the code.

3. Design files summary

Complete a separate row for each design file associated with your hardware (including the primary design files). Any empty rows should be deleted.

Design file name | File type | Open source license | Location of the file
For example: Design file 1 | e.g., CAD files, figures, videos | All designs must be submitted under an open hardware license. Enter the corresponding open source license for the file. | Either enter the URL for the repository or the sentence: "Available with the article".

For each design file listed in the summary table above, include a short description of the file below (just one or two sentences per design file).

Bill of materials

If your bill of materials is long or complex, you can upload the details in an editable spreadsheet, e.g., ODS file type, Excel spreadsheet or PDF file, to an open access online location, such as the Open Science Framework (https://osf.io/) repository. Include the link here. Alternatively, the bill of materials can be submitted alongside your manuscript as supplementary material.

4. Bill of materials summary

Complete a separate row for each component of your hardware – all components associated with a cost should be listed and any empty rows should be deleted.

Designator | Component | Number | Cost per unit -currency | Total cost - currency | Source of materials | Material type
If possible, use the same designator here as you use in the associated design file. If that’s not possible, you will need to explain the relationship between the two. | Name of Component 1 | Number of units | Cost per unit and the currency used | Total cost and the currency used | If possible, include a direct link to a webpage where the component can be purchased | Select from: -Metal -Semi-conductor -Ceramic -Polymer -Biomaterial -Organic -Inorganic -Composite -Nanomaterial -Semiconductor -Non-specific -Other

You can use this space for any additional descriptions of the materials used.

5. Build instructions

Provide detailed, step-by-step construction instructions for the submitted hardware:

- Include all necessary information for reproducing it.
- Explain and (when possible) characterize design decisions. Include any design alternatives you created.
- Use visual instructions such as schematics, images and videos.
- Clearly reference design files and component parts described in the Design file summary and the Bill of materials summary.
- Highlight any potential safety concerns.
6. Operation instructions

Provide detailed, step-by-step instructions for the safe and proper operation of the hardware.

- Use visual instructions, as necessary.
- Highlight any potential safety hazards.
7. Validation and characterization

Demonstrate the operation of the hardware and characterize its performance for a specific scientific application.

- Highlight a relevant use case.
- If possible, characterize performance of the hardware over operational parameters.
- Create a bulleted list describing the capabilities (and limitations) of the hardware. For example, load and operation time, spin speed, coefficient of variation, accuracy, precision, etc.

Ethics statements

HardwareX has ethical guidelines that all authors must comply with. In addition, we ask you to complete the relevant statement(s) below. Please delete those which are not relevant for your work.

If your work involved human subjects, please include a statement here confirming that the relevant informed consent was obtained from those subjects:

If your work involved animal experiments, please include a statement here confirming that those experiments complied with the ARRIVE guidelines (https://www.nc3rs.org.uk/arrive-guidelines) and were carried out in accordance with the U.K. Animals (Scientific Procedures) Act, 1986 and associated guidelines; EU Directive 2010/63/EU for animal experiments (http://ec.europa.eu/environment/chemicals/lab_animals/legislation_en.htm); or the National Institutes of Health guide for the care and use of laboratory animals (NIH Publications No. 8023, revised 1978). Note, the sex of the animals must be indicated, and, where appropriate, the influence (or association) of sex on the results of the study:

CRediT author statement

CRediT is in initiative that enables authors to share an accurate and detailed description of their diverse contributions to a published work.

Example of a CRediT author statement:

Michael Anderson: Conceptualization, Methodology, Software, Writing- Original draft preparation Dennis Yaskevich: Visualization, Methodology, Validation, Jose Yeste Lozano: Methodology, Validation. Jay Thiagarajah: Supervision, Writing- Reviewing and Editing, Funding Acquisition.

Please add a CRediT author statement for your data article here, using the categories listed on this web (https://www.elsevier.com/authors/journal-authors/policies-and-ethics/credit-author-statement)page.

Acknowledgments

All contributors who do not meet the criteria for authorship should be listed in an acknowledgments section.

In addition, please list any funding sources in this section. List funding sources in this standard way to facilitate compliance to funder's requirements:

Funding: This work was supported by the National Institutes of Health [grant numbers xxxx, yyyy]; the Bill & Melinda Gates Foundation, Seattle, WA [grant number zzzz]; and the United States Institutes of Peace [grant number aaaa].

It is not necessary to include detailed descriptions on the program or type of grants and awards. When funding is from a block grant or other resources available to a university, college, or other research institution, submit the name of the institute or organization that provided the funding.

If no funding has been provided for the research, please include the following sentence:

This research did not receive any specific grant from funding agencies in the public, commercial, or not-for-profit sectors.

References:

If relevant, you should include a reference to the original publication of the hardware you customized and a reference to the repository in which your design files are published. Other references can be included, as required; for example, references that put your device in context in the literature. For more information on the reference format in HardwareX please see the Guide for Authors (https://www.elsevier.com/journals/hardwarex/2468-0672/guide-for-authors).

______________________________________________________________________

Additional Information for authors. (do not include these lines in your submission)

Author manuscript checklist

- Is the subject of the submission under an open source license? Are design files in the preferred format for making modifications as defined by the Open (http://www.oshwa.org/definition/) (http://www.oshwa.org/definition/)Source (http://www.oshwa.org/definition/) (http://www.oshwa.org/definition/)Hardware (http://www.oshwa.org/definition/) (http://www.oshwa.org/definition/)definition (http://www.oshwa.org/definition/)?
- Can the hardware be reproduced with the details provided in the submission?
- Are all relevant design files available on either the Mendeley Data, Open Science Framework, or Zenodo repository? Are they described in the Design Files Summary, and clearly documented? (E.g., descriptive file names, commented code, labeled images, etc.)
  - If in the Open Science Framework, has the repository been registered? Instructions (https://osf.io/wgk7q/wiki/home/)
  - If in Zenodo, is the repository open access and published? Instructions (https://doi.org/10.5281/zenodo.3346799)
  - If in Mendeley Data, is the repository published or the sharable link included in the additional information you plan to submit? Instructions (https://doi.org/10.5281/zenodo.3346799)
- Are visual instructions used when necessary?
- Is the utility of the hardware to the scientific community explained clearly? Has a specific scientific application been demonstrated using the hardware?
- Is the performance of the hardware adequately demonstrated and characterized?
- Are all potential safety concerns addressed?
- For more information on the article template consult the Guide (https://www.elsevier.com/journals/hardwarex/2468-0672/guide-for-authors) (https://www.elsevier.com/journals/hardwarex/2468-0672/guide-for-authors)to (https://www.elsevier.com/journals/hardwarex/2468-0672/guide-for-authors) (https://www.elsevier.com/journals/hardwarex/2468-0672/guide-for-authors)Authors (https://www.elsevier.com/journals/hardwarex/2468-0672/guide-for-authors).

Reminder: Before you submit, please delete all

the instructions in this document (the text in italics), including this paragraph.

Thank you!

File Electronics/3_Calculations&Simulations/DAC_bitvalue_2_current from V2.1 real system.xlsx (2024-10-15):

DAC bit value | V drop over resistor | Current (uA)
3139 | 677 | 98.97660819
2593 | 341 | 49.85380117
2156 | 67.78 | 9.909356725
2145 | 60.9 | 8.903508772
2134 | 53.9 | 7.880116959
2123 | 47 | 6.871345029
2113 | 40.9 | 5.979532164
2102 | 34 | 4.970760234
2091 | 27.1 | 3.961988304
2080 | 20.3 | 2.967836257
2069 | 13.5 | 1.973684211
2058 | 6.7 | 0.9795321637
2036 | -7 | -1.023391813
1501 | -340.2 | -49.73684211
955 | -676 | -98.83040936

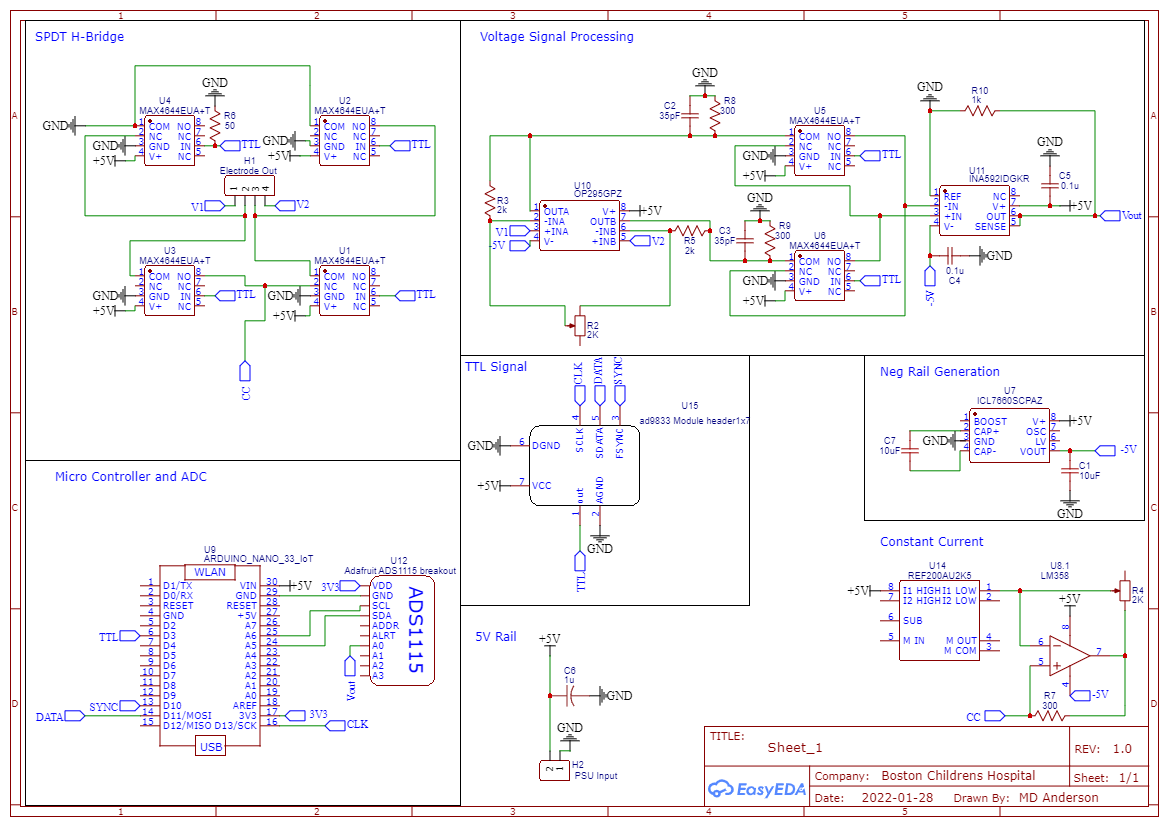
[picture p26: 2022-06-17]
docs/images/Schematic_Flexi-TEER_2022-04-20001.png

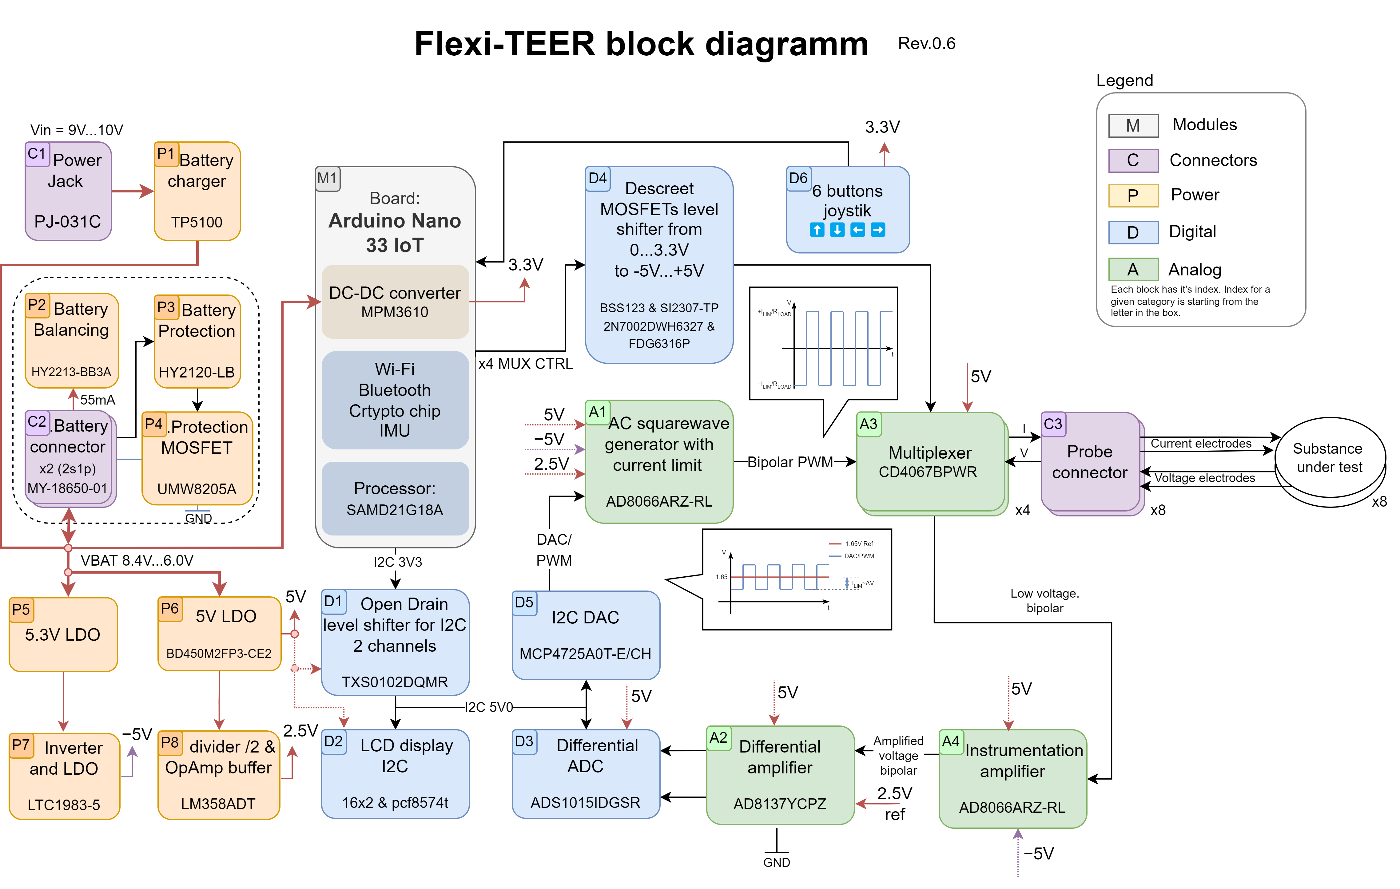
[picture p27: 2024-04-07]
Electronics/2_Block-diagram/Flexi-TEER_rev0.6.png

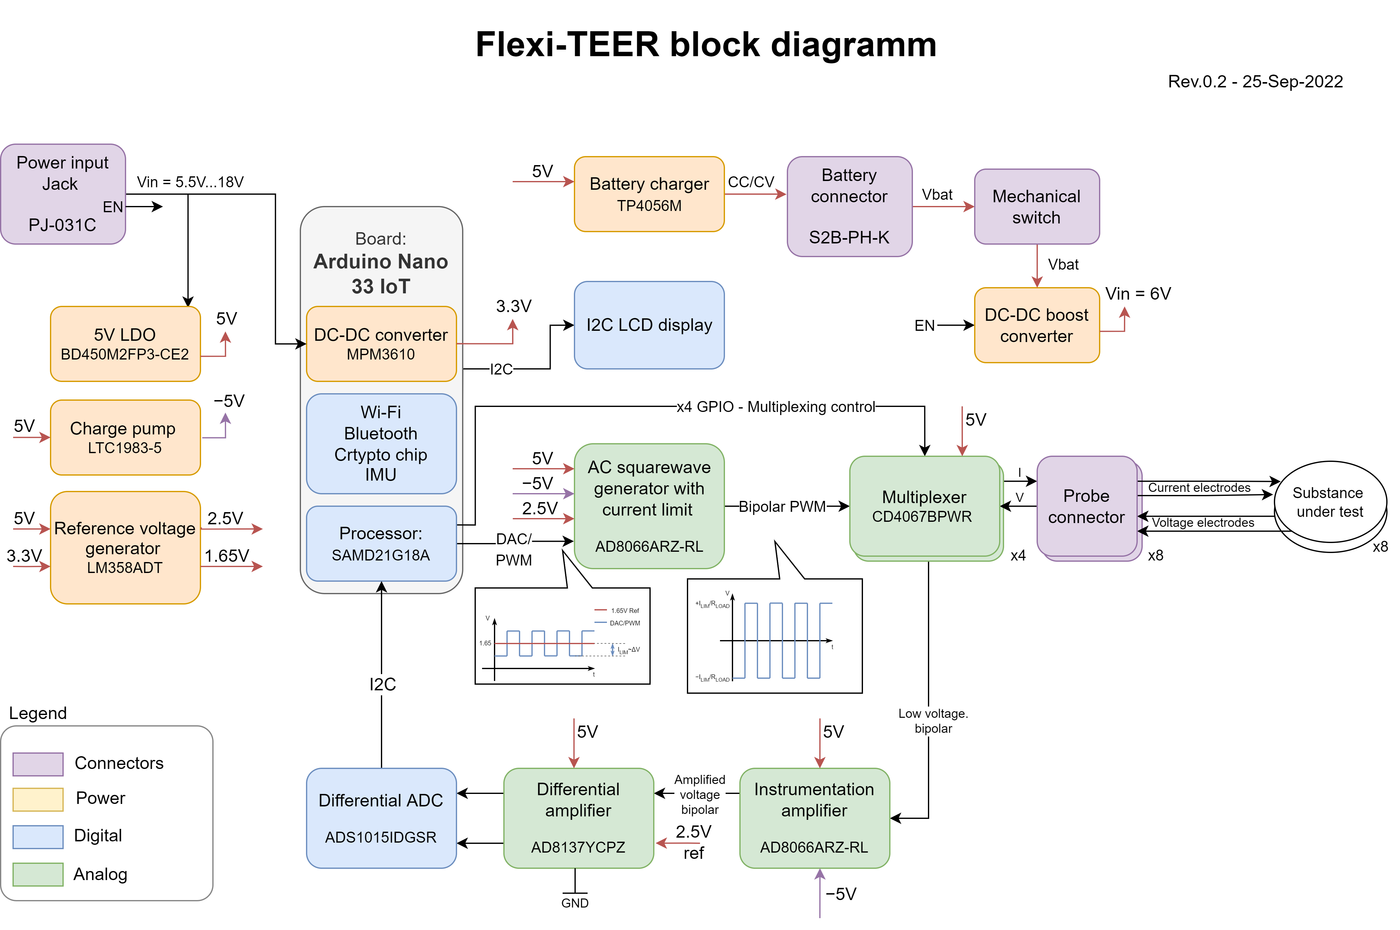
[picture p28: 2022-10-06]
Electronics/2_Block-diagram/Flexi-TEER_rev0.2.png

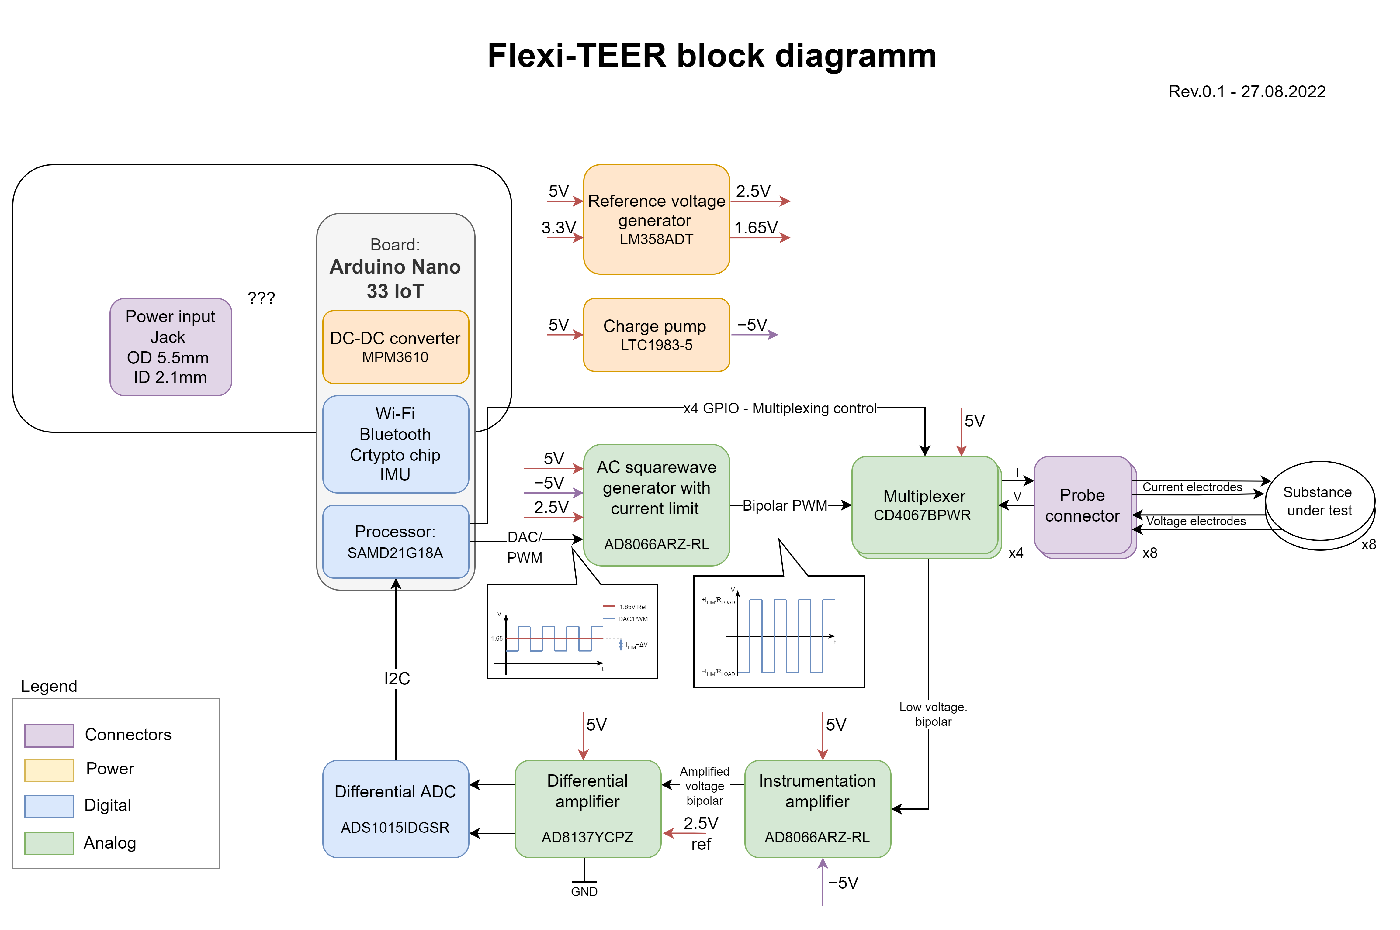
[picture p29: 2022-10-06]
Electronics/2_Block-diagram/Flexi-TEER_rev0.1.png

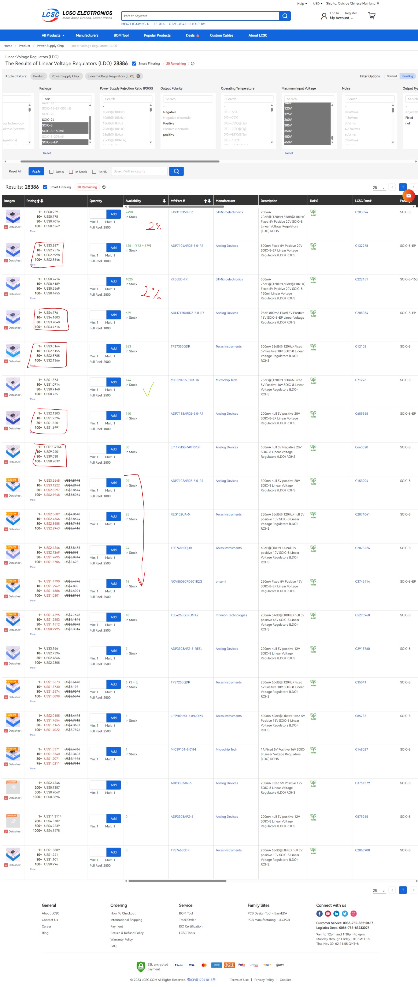
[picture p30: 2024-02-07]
Electronics/4_Schematic/P6_5VLDO_selection_www.lcsc.com.jpeg

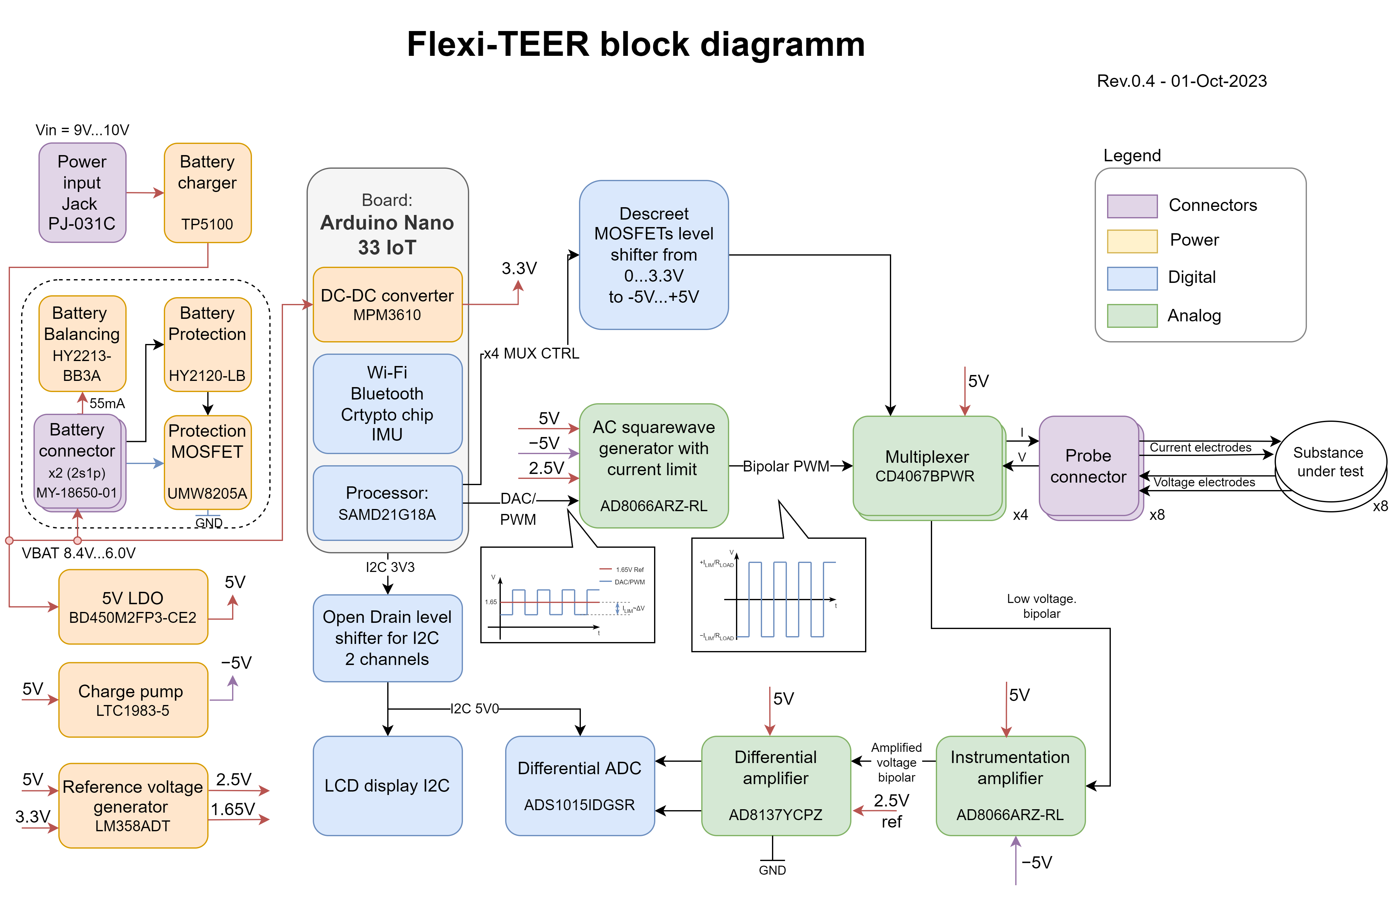
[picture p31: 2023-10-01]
Electronics/2_Block-diagram/Flexi-TEER_rev0.4.png

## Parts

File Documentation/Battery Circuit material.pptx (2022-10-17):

## Battery Circuit

## Idea

- Lithium batteries are finicky and need current regulators and overcharge protections to charge safely
- One cell batteries are much easier to get and much cheaper. Boosting voltage to 5V is needed for 5V logic circuits.
- Charging ICs use current to determine if battery is charged or not. To accomplish this the load should be disconnected when DC power is given to the instrument. A p-MOSFET IC is a nice solution to this.

## Common breakout board

- Breakout board are nice references as they are inclusive units. Here is a common schematic of one.

We have the TP4056 chip currently, but are missing the over voltage protection IC and the N-MOSFET which I believe switches power on and off to the battery as needed (not certain here). Here is a video about it: https://www.youtube.com/watch?v=Fj0XuYiE7HU
Also no temp protection is needed as it will be used in room temp situations.

## Load switching

- We need to disconnect the battery when DC power is added so that the DC power runs the device and separately charges the battery.
- This is an article about the issue: https://www.best-microcontroller-projects.com/tp4056-page2.html. Basically, one p-MOSFET disconnects the battery from load circuit. The other disconnects the DC from the load circuit. If hooked up in a certain way, it will make sure only one if connected to the load at a time and at the same time, the battery and DC are not connected directly themselves.
- AO4803A is a dual channel p-mosfet which appears suitable for load switching according to its data sheet.

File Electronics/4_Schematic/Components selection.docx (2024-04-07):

# Components selection doc

28 NOV 2023 Dennis Yaskevich

This document provides background on some components selection for the project to be available for future reference and understanding of decision making.

Headings in this documents are numbered by the Electrical block diagram numbers.
The latest version of the Block diagram should be available under the following path:
<repository root>\Electronics\2_Block-diagram

## General guidelines

When selecting components for this project the following guidelines have to be followed:

1. Use hand-solder friendly packages
  a. use 0603 SMD packages for passive components
2. Select components that require software based on libraries availability to avoid writing them
3. Select components for Analog section not looking at the cost (it will be optimized later)
4. When possible use “jelly beans parts” => pick general components (like power supplies) that support multiple manufacturers parts on the same footprint.
5. Components should be available in LSCS stock and be suitable for JLCPCB SMT serivce

## Block P6. Selecting 5V LDO

#### Requirements for 5V LDO:

1. Expected values of current to be sinked from the LDO is 147mA based on <repository root>\Electronics\3_Calculations&Simulations\Power Table.xlsx
2. Fixed 5.0V output voltage 1% precision
3. Maximum input voltage should be above 10V (supplied from x2 4.2V li-ion batteries)
4. 5V LDO must have EN pin to be able to turn off all downstream devices with single GPIO
5. Low quiescent current is desired feature to not drain the battery as much when disabled.
6. Relative modern IC is desired to have improved PSSR speak and control loop stability

Component used in Hardware rev2 HT7550-1 is rejected because of missing EN pin. -> ~~SOT-89~~~~, SOT23-3~~

Based on guideline 4 industry standard package must be selected.
Based on requirement 1, it would be good to pick LDO with at least 300mA maximum output current. 500mA is best. -> ~~SOT23-5~~

#### Investigation of LDOs available in SOIC8 & HVSOP8 packages

TI selector search filter: https://www.ti.com (https://www.ti.com/power-management/linear-regulators-ldo/products.html)

Onsemi selector search filter: https://www.onsemi.com (https://www.onsemi.com/products/power-management/linear-regulators-ldo)

Diodes search filter: https://www.diodes.com/ (https://www.diodes.com/products/power-management/linear-and-low-dropout-ldo-regulators/)

LCSC search filter: https://www.lcsc.com (https://www.lcsc.com/products/Linear-Voltage-Regulators-LDO_387.html) (see as per 29 Nov P6_5VLDO_selection_www.lcsc.com.jpeg)

Pinout | Available MPNs (datasheet) | Key specs | Comment

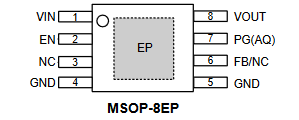
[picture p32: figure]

| tps7b82-q1 (https://www.ti.com/lit/ds/symlink/tps7b82-q1.pdf?ts=1701173973833) | | Not available LCSC
| AP7583Q_AQ (https://www.diodes.com/assets/Datasheets/AP7583Q_AQ.pdf) | | Not available LCSC

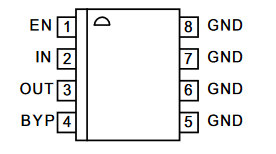
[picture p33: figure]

| MIC49150 (https://ww1.microchip.com/downloads/en/DeviceDoc/mic49150.pdf) MIC5219 (https://ww1.microchip.com/downloads/en/DeviceDoc/MIC5219-500mA-Peak-Output-LDO-Regulator-DS20006021A.pdf) MIC39101 (https://datasheet.lcsc.com/lcsc/2304140030_Microchip-Tech-MIC39101-5-0YM_C148027.pdf) | Other options from Microchip, just for reference | Not available LCSC
| MIC5209 (https://ww1.microchip.com/downloads/en/DeviceDoc/20005720A.pdf) | 1% at 25, Fixed output V | 144 pcs stock, 1.37$
| spx3819 (https://assets.maxlinear.com/web/documents/spx3819.pdf) | 1% at 25, Fixed output V | No stock
| TL5209DR (https://datasheet.lcsc.com/lcsc/2001050532_Texas-Instruments-TL5209DR_C478073.pdf) | 1% | EOL part in stock just for reference
| AP2213 (https://www.diodes.com/assets/Datasheets/AP2213.pdf) | Only available in 3V3 output V

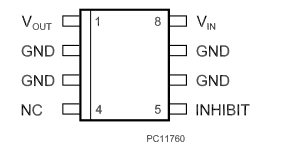
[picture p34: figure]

| TLV767 (https://www.ti.com/lit/ds/symlink/tlv767.pdf?ts=1701182486065) | | No stock
| KFXX (https://datasheet.lcsc.com/lcsc/2304140030_STMicroelectronics-KF50BD-TR_C222151.pdf) | 2% tolerance
| ADP7104 (https://datasheet.lcsc.com/lcsc/2304140030_Analog-Devices-ADP7104ARDZ-5-0-R7_C132278.pdf) | | High cost
| L4931CD50 (https://www.lcsc.com/product-detail/Linear-Voltage-Regulators-LDO_STMicroelectronics-L4931CD50-TR_C283394.html) | 2% tolerance
| TPS767 (https://www.ti.com/lit/ds/symlink/tps767.pdf?ts=1701210948468) | 2% tolerance | No stock
| NCP3334 (https://www.onsemi.com/download/data-sheet/pdf/ncp3334-d.pdf) | 0.9% tol, only adjustible is available | 1773 stock 0.8$
| TPS7350QDR (https://datasheet.lcsc.com/lcsc/2304140030_Texas-Instruments-TPS7350QDR_C12102.pdf) | 2% tolerance | 263 in stock 3$

MIC5209-5.0YM-TR has been selected (lcsc (https://www.lcsc.com/product-detail/Linear-Voltage-Regulators-LDO_Microchip-Tech-MIC5209-5-0YM-TR_C71226.html)).

## Block P5. Selecting 5.3V LDO

#### Requirements for 5V LDO:

1. Expected values of current to be supplied is below 50mA, any package is fine
2. EN feature is required to be able to disable negative supply

This part is very generic and easy to pick.

Diodes search filter: https://www.diodes.com/ (https://www.diodes.com/products/power-management/linear-and-low-dropout-ldo-regulators/)

LCSC search filter: www.lcsc.com (https://www.lcsc.com/products/Linear-Voltage-Regulators-LDO_387.html)

Pinout | Available MPNs (datasheet) | Key specs | Comment

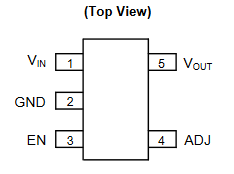
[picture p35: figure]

| AP2202 (https://datasheet.lcsc.com/lcsc/2004082232_Diodes-Incorporated-AP2202K-ADJTRG1_C507873.pdf) | 1%, 150mA, En | 0.14$ 3k in stock
| AP2210 (https://www.diodes.com/assets/Datasheets/AP2210.pdf) | 1%, 300mA, En | 0.12$ 2k in stock
| SPX3819M5 (https://datasheet.lcsc.com/lcsc/1806151814_MaxLinear-SPX3819M5-L-TR_C9056.pdf) | 1%, 500mA, En | In stock
| TPS76301DBVR (https://datasheet.lcsc.com/lcsc/1809151115_Texas-Instruments-TPS76301DBVR_C7727.pdf) | 1%, 150mA, En | In stock

AP2210 is selected.

## Block P7. Selecting the load resistor for negative voltage gen

According to testing documented in the bring up report, the negative voltage generator features some additional noise caused by Pulse skipping mode that is enabled at light load.

Changing the component is too big of a change for the minor revision and it’s not target of MVP. Quick workaround is adding 220 Ohm resistor as “dummy load” to consume additional current and avoid enabling the light load mode.

VOUT = -5 V

R = 220 Ω

P = VOUT²R = (-5 V)²220 Ω = 0.114 W

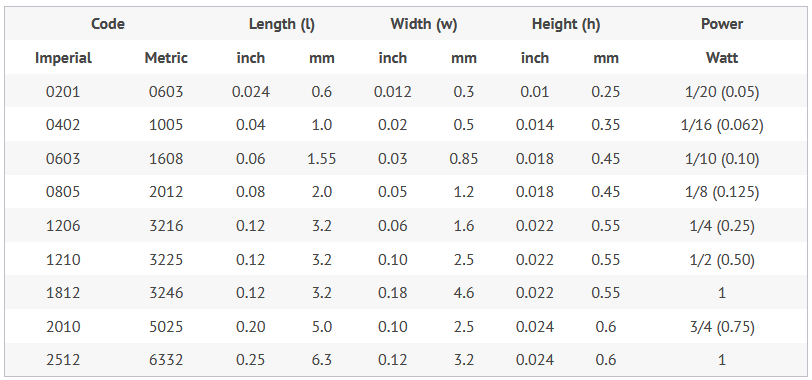
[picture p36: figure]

It would be safe to have at least 2 times power rating compared to the calculated power.

I would go with 1206 resistor

## Block P1. Batteries charger

Tp4056 is proven low cost solution for battery charging for single cell. It’s commonly used as IC and as breakout PCB. In this design 2 batteries connected in series must be charged. The first idea is to check the 2 cell version of TP4056:
- TP5100 the battery charger IC for 2 cells in series from this same manufacturer

Problems:

- TP5100 does not support dual sourcing.
- it does not have the hand soldering friendly package.

Alternative circuit for P1 block is the battery charger based on LM317 LDO (https://www.ti.com/lit/ds/symlink/lm317.pdf). This is dual sourcable jelly bean part that supports batteries charging. But in default configuration it does not support CC CV battery charging

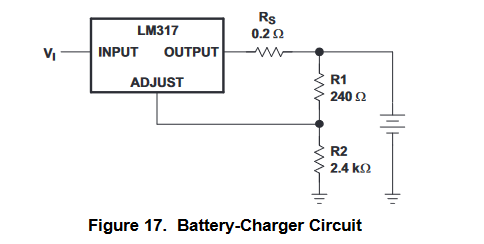
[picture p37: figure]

There is another configuration that is supposed to handle it, but it require careful simulation and test

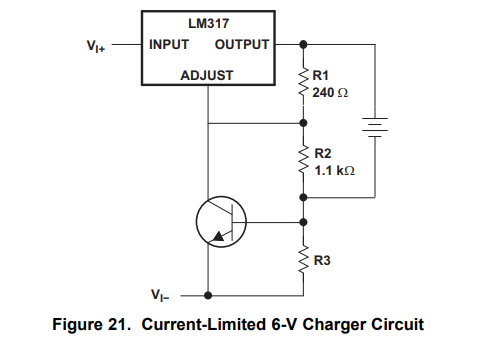
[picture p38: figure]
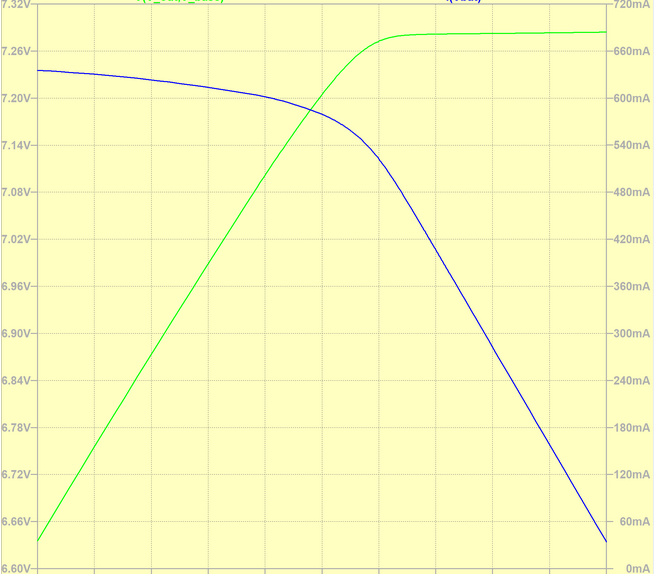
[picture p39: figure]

https://electronics.stackexchange.com/questions/503642/lithium-ion-battery-charger-using-lm317

For now I’m skipping the LM317 and keep TP5100 in the design. This IC must be replaced in the subsequent releases of the Flexi-Teer by some linear battery charging solution but for now it stays on SCH simply as something that works.

Schematic is implemented according to the ref. design from the datasheet. But unfortunatley tehre are a few different datasheets out there with different typical application circuits:

- <repo root>/Electronics/1_Datasheets/Charger_TP5100.pdf (http://toppwr.com/uploadfile/file/20230304/6402f53e7e8d9.pdf)

Reference schematic from official datasheet


TS Pin to battery NTC (Negative temperature coefficient thermistor) sensor

In case TS Less than the voltage at pin VREG of 45% or greater than VREG Voltage 80% It means that the battery temperature is too low or too high, the charging is suspended. in case TS Direct access GND Battery temperature detection function is canceled, the charging function properly.

Alternative implementation of the temperature sense feature.


This schematic illustrates how to implement “Power Path” feature


In the datasheet I found when working on rev.2.0 of FlexiTeer 10V were specified as maximum VIN.

Now in all datasheets I can see 12V input voltage but I would still keep 9V power supply as we already bought it. +I already tested this IC with 9V power supply.
Yes, it produces audible noise and it would be nice to check if it’s still the case with 12V iput

Also it would be nice to check if adding 0.2 Ohm before the charger changes anything.

PWR_ON and CS pins also must be checked. Check how PWR_ON works when CS is 0

Measure VREG. Make sure CS works from 3V3

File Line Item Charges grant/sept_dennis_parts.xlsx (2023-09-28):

# | QUANTITY | PART NUMBER | MANUFACTURER PART NUMBER | DESCRIPTION | CUSTOMER REFERENCE | BACKORDER | UNIT PRICE | EXTENDED PRICE
1 | 1 | 1050-ABX00027-ND | ABX00027 | ARDUINO NANO 33 IOT |  | 0 | 23.49 | 23.49
2 | 1 | 102-SWH15-9-EB-P5-ND | SWH15-9-EB-P5 | AC/DC WALL MOUNT ADAPTER 9V 14W |  | 0 | 14.23 | 14.23
3 | 1 | 4411-CN0295D-ND | CN0295D | 1602 I2C LCD |  | 0 | 8.24 | 8.24
4 | 10 | 732-12542-ND | 709440800 | SNAP-ON STOP SPACER REVERSE MOUN |  | 0 | 0.192 | 1.92
5 | 10 | 732-12936-ND | 971150244 | BRASS SPACER STUD METRIC THREAD |  | 0 | 0.826 | 8.26
6 | 10 | 145-50M020040G004-ND | 50M020040G004 | FILLISTER PHILLIPS SCREW, M2 X . |  | 0 | 0.1 | 1.00
7 | 10 | RPC7084-ND | 04M020040HN | HEX NUT, NATURAL, NYLON, M2 X .4 |  | 0 | 0.101 | 1.01
8 | 10 | 1276-1034-1-ND | CL10A105KO8NNNC | CAP CER 1UF 16V X5R 0603 |  | 0 | 0.03 | 0.30
9 | 5 | AP2120N-3.3TRG1DICT-ND | AP2120N-3.3TRG1 | IC REG LINEAR 3.3V 150MA SOT23 |  | 0 | 0.35 | 1.75
10 | 5 | ATSAMD11C14A-SSUTCT-ND | ATSAMD11C14A-SSUT | IC MCU 32BIT 16KB FLASH 14SOIC |  | 0 | 1.46 | 7.30

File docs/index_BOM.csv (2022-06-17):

Name in documentation | Qty | Full Name | Supplier 1 | Part No | Link
0.1uF SMD Capacitor | 2 | capacitor_603 | Amazon | B09SFT7L731 | https://www.amazon.com/CenryKay-Soldering-Electric-Universal-Pack%EF%BC%88Silver%EF%BC%89/dp/B09SFT7L73
10uF SMD Capacitor | 2 | capacitor_603 | Amazon | B09SFT7L731 | https://www.amazon.com/CenryKay-Soldering-Electric-Universal-Pack%EF%BC%88Silver%EF%BC%89/dp/B09SFT7L73
10x1 Female Pin Header | 1 | Female_pin_headers | Amazon | B07CWSXY7P | https://www.amazon.com/Glarks-Connector-Assortment-Stackable-Breakaway/dp/B07CWSXY7P?hvadid=309881068962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
16x1 Female Pin Header | 2 | Female_pin_headers | Amazon | B07CWSXY7P | https://www.amazon.com/Glarks-Connector-Assortment-Stackable-Breakaway/dp/B07CWSXY7P?hvadid=309881068962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
1k SMD Resistor | 1 | resistor_603 | Amazon | B09SFT7L731 | https://www.amazon.com/CenryKay-Soldering-Electric-Universal-Pack%EF%BC%88Silver%EF%BC%89/dp/B09SFT7L73
2k SMD Resistor | 2 | resistor_603 | Amazon | B09SFT7L731 | https://www.amazon.com/CenryKay-Soldering-Electric-Universal-Pack%EF%BC%88Silver%EF%BC%89/dp/B09SFT7L73
300 SMD Resistor | 3 | resistor_603 | Amazon | B09SFT7L731 | https://www.amazon.com/CenryKay-Soldering-Electric-Universal-Pack%EF%BC%88Silver%EF%BC%89/dp/B09SFT7L73
35pF SMD Capacitor | 2 | capacitor_603 | Amazon | B09SFT7L731 | https://www.amazon.com/CenryKay-Soldering-Electric-Universal-Pack%EF%BC%88Silver%EF%BC%89/dp/B09SFT7L73
50 SMD Resistor | 1 | resistor_603 | Amazon | B09SFT7L731 | https://www.amazon.com/CenryKay-Soldering-Electric-Universal-Pack%EF%BC%88Silver%EF%BC%89/dp/B09SFT7L73
7x1 Female Pin Header | 1 | Female_pin_headers | Amazon | B07CWSXY7P | https://www.amazon.com/Glarks-Connector-Assortment-Stackable-Breakaway/dp/B07CWSXY7P?hvadid=309881068962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
Curved Soldering Iron Tip | 1 | OP295GPZ OP Amp | Amazon | B09SFT7L731 | https://www.amazon.com/CenryKay-Soldering-Electric-Universal-Pack%EF%BC%88Silver%EF%BC%89/dp/B09SFT7L73
INA592 Diff Amp | 1 | INA592IDGKR difference amp | Amazon | B09SFT7L731 | https://www.amazon.com/CenryKay-Soldering-Electric-Universal-Pack%EF%BC%88Silver%EF%BC%89/dp/B09SFT7L73
LM358 OP Amp | 1 | LM358 OP Amp | Amazon | B09SFT7L731 | https://www.amazon.com/CenryKay-Soldering-Electric-Universal-Pack%EF%BC%88Silver%EF%BC%89/dp/B09SFT7L73
REF200 Current Source | 1 | REF200AU2K5 current sink | Amazon | B09SFT7L731 | https://www.amazon.com/CenryKay-Soldering-Electric-Universal-Pack%EF%BC%88Silver%EF%BC%89/dp/B09SFT7L73
SPDT Switch | 6 | MAX4644EUAT SPDT switch | Amazon | B09SFT7L731 | https://www.amazon.com/CenryKay-Soldering-Electric-Universal-Pack%EF%BC%88Silver%EF%BC%89/dp/B09SFT7L73
Straight Soldering Iron Tip | 1 | ARDUINO_NANO_33_IoT | Amazon | B09SFT7L731 | https://www.amazon.com/CenryKay-Soldering-Electric-Universal-Pack%EF%BC%88Silver%EF%BC%89/dp/B09SFT7L73

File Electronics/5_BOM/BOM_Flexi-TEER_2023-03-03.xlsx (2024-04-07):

ID | Name | Designator | Footprint | Quantity | Manufacturer Part | Manufacturer | Supplier | Supplier Part | Price per piece | Price per PCB
1 | MY-18650-01 | BT3,BT4,BT5,BT6 | BAT-TH_MY-18650-01 | 4 | MY-18650-01 | MYOUNG(美阳) | LCSC | C2979183 | $0.31 | $1.24
2 | 10u | C1,C2,C3,C4,C28,C29,C30 | C0805 | 7 | CL21A106KOQNNNE | SAMSUNG(三星) | LCSC | C1713 | $0.01 | $0.08
3 | 0.1u | C5,C6,C9,C10,C13,C14,C15,C16,C17,C20,C21,C22,C23,C24,C25,C26,C38,C39,C40,C44,C45,C50,C51,C52,C54,C56,C58 | C0603 | 27 | CL10B104KO8NNNC | SAMSUNG(三星) | LCSC | C66501 | $0.0028 | $0.08
4 | 1nF | C7,C8,C11,C12,C18,C19 | C0603 | 6 | CC0603KRX7R7BB102 | YAGEO(国巨) | LCSC | C519403 | $0.0031 | $0.02
5 | 4.7uF | C27,C49 | C0603 | 2 | CL10A475KO8NNNC | SAMSUNG(三星) | LCSC | C19666 | $0.01 | $0.02
6 | 1uF | C48 | C0603 | 1 | CL10A105KO8NNNC | SAMSUNG(三星) | LCSC | C1592 | $0.0034 | $0.0034
7 | DC-005-20A_C136744 | CON1 | DC-IN-TH_DC-005-20A | 1 | DC-005-20A | 韩国韩荣 | LCSC | C136744 | $0.11
8 | PM254-1-15-Z-8.5 | CON2,CON3 | HDR-TH_15P-P2.54-V-F | 2 | PM254-1-15-Z-8.5 | HCTL(华灿天禄) | LCSC | C2897378 | $0.23 | $0.02
9 | FH-00133 | CON4 | HDR-TH_4P-P2.54-V-F | 1 | FH-00133 | Liansheng(连盛) | LCSC | C2685089 | $0.05 | $2.63
10 | SS34BF_C64883 | D4 | SMBF_L4.3-W3.6-LS5.3-RD | 1 | SS34BF | MDD | LCSC | C64883 | $0.04 | $0.25
11 | Nut_M2 | H2,H3,H4,H5 | KEYSTONE_1902C | 4 |  | Essentra Components | Digi-Key | 04M020040HN | $0.14 | $1.84
12 | Screw_M2_5mm | H6,H7,H8,H9 | KEYSTONE_1902C | 4 |  | Essentra Components | Digi-Key | 50M020040G004 | $0.14 | $0.11
13 | 10uH | L4 | IND-SMD_L7.1-W6.6 | 1 | MDA7030-100M | KOHERelec(科或) | LCSC | C2847485 | $0.63 | $0.01
14 | 17-21SYGC/S530-E2/TR8 | LED5 | LED0805-RD | 1 | 17-21SYGC/S530-E2/TR8 | EVERLIGHT | LCSC | C73548 | $0.02 | $0.01
15 | XL-2012UOC | LED6 | LED0805-RD_ORANGE | 1 | XL-2012UOC | XINGLIGHT(成兴光) | LCSC | C965813 | $0.01 | $0.01
16 | SI2307-TP | Q1,Q2,Q6,Q7,Q10 | SOT-23-3_L2.9-W1.3-P1.90-LS2.4-BR | 5 | SI2307-TP | MCC(美微科) | LCSC | C668998 | $0.08 | $0.01
17 | BSS123 | Q3,Q4,Q8 | SOT-23-3_L2.9-W1.6-P1.90-LS2.8-BR | 3 | BSS123 | CJ（江苏长电/长晶） | LCSC | C79015 | $0.03 | $0.13
18 | UMW8205A | Q5 | SOT-23-6_L2.9-W1.6-P0.95-LS2.8-BL | 1 | UMW8205A | Youtai Semiconductor Co., Ltd. | LCSC | C351449 | $0.07 | $0.24
19 | 100k | R2,R3,R20,R21,R23,R24,R25,R26,R27,R30,R31,R40 | R0603 | 12 | RC0603FR-07100KL | YAGEO(国巨) | LCSC | C14675 | $0.001 | $0.08
20 | 4.7k | R4,R5,R22,R28,R29,R35,R39,R42,R44,R45,R46,R47,R65,R71,R72,R78,R79 | R0603 | 17 | RC0603FR-074K7L | YAGEO(国巨) | LCSC | C99782 | $0.0013 | $0.01
21 | 1k | R6,R8,R13,R14,R15,R16,R17,R18 | R0603 | 8 | 0603WAF1001T5E | UNI-ROYAL(厚声) | LCSC | C21190 | $0.0006 | $2.08
22 | 2k | R7,R9,R11,R12,R64 | R0603 | 5 | 0603WAF2001T5E | UNI-ROYAL(厚声) | LCSC | C22975 | $0.001 | $0.02
23 | 499 | R10 | R0603 | 1 | RC0603FR-07499RL | YAGEO(国巨) | LCSC | C137714 | $0.0012 | $0.01
24 | 1k0, 0.1% | R19 | R0603 | 1 | RT0603BRD071KL | YAGEO(国巨) | LCSC | C110776 | $0.02 | $0.01
25 | 75 | R32,R33 | R2512 | 2 | 0603WAF750JT5E | UNI-ROYAL(厚声) | LCSC | C4275 | $0.0011 | $0.01
26 | 47k | R41 | R0603 | 1 | 0603WAF4702T5E | UNI-ROYAL(厚声) | LCSC | C25819 | $0.001 | $0.01
27 | 102k | R48 | R0603 | 1 | RC0603FR-07100KL | YAGEO(国巨) | LCSC | C14675 | $0.001 | $0.01
28 | 316k | R49 | R0603 | 1 | RC0603FR-07316KL | YAGEO(国巨) | LCSC | C185340 | $0.0014 | $0.01
29 | 330 | R50,R51,R52,R53,R54,R55,R62,R63 | R0603 | 8 | 0603WAF3300T5E | UNI-ROYAL(厚声) | LCSC | C23138 | $0.001 | $0.01
30 | 100 | R60,R61 | R0603 | 2 | 0603WAF1000T5E | UNI-ROYAL(厚声) | LCSC | C22775 | $0.0011 | $0.01
31 | 0.1 | R66 | R1206 | 1 | 1206W4J010KT5E | UNI-ROYAL(厚声) | LCSC | C247459 | $0.01 | $0.05
32 | 51k | R67 | R0603 | 1 | 0603WAF5102T5E | UNI-ROYAL(厚声) | LCSC | C23196 | $0.001 | $0.03
33 | 20k | R73,R74 | R0603 | 2 | 0603WAF2002T5E | UNI-ROYAL(厚声) | LCSC | C4184 | $0.001 | $0.63
34 | 7.5k | R75,R76 | R0603 | 2 | 0603WAF7501T5E | UNI-ROYAL(厚声) | LCSC | C23234 | $0.001 | $0.46
35 | 5k | R77 | R0603 | 1 | AR03BTCX5001 | Viking(光颉) | LCSC | C2828621 | $0.03 | $1.24
36 | R-RJ45R08P-8000 | RJ1,RJ2 | RJ45-TH_R-RJ45R08P-8000 | 2 | R-RJ45R08P-8000 | Shenzhen Cankemeng | LCSC | C386760 | $2.00 | $0.07
37 | STUD_M2_15mm | S1,S2,S3,S4 | STANDOFF+SCREW_M2 | 4 |  | Würth Elektronik | Digi-Key | 971150244 | $0.95 | $0.52
38 | Board Support | S5,S6,S7,S8 | STANDOFF+SCREW_M2 | 4 |  | Würth Elektronik | Digi-Key | 709440800 | $0.23 | $1.36
39 | TS-1095-A2B2-D1 | SW1,SW2,SW3,SW4,SW5,SW7 | SW-TH_4P-L6.0-W6.0-P4.50-LS6.5 | 6 | TS-1095-A2B2-D1 | Yuandi(元迪) | LCSC | C782805 | $0.04 | $4.01
40 | HEF4067BT,653 | U1,U6,U7,U10 | SO-24_L15.4-W7.5-P1.27-LS10.3-BL | 4 | HEF4067BT,653 | Nexperia | LCSC | C551465 | $1.05 | $0.01
41 | AD8066ARZ-RL | U2,U29 | SOIC-8_L5.0-W4.0-P1.27-LS6.0-BL | 2 | AD8066ARZ-RL | Analog Devices | LCSC | C652280 | $4.41 | $0.01
42 | LM27761DSGR | U3 | WSON-8_L2.0-W2.0-P0.65-BL-EP | 1 | LM27761DSGR | TI(德州仪器) | LCSC | C129351 | $1.84 | $0.02
43 | AD8137YCPZ-REEL7 | U4 | LFCSP-8_L3.0-W3.0-P0.50-BL-EP-1 | 1 | AD8137YCPZ-REEL7 | Analog Devices | LCSC | C112004 | $2.63 | $4.22
44 | ADS1015IDGSR | U5 | VSSOP-10_L3.0-W3.0-P0.50-LS4.9-BL | 1 | ADS1015IDGSR | Texas Instruments | LCSC | C193969 | $2.08 | $0.04
45 | ARDUINO_NANO_33_IoT | U8 | ARDUINO_NANO_33_IOT | 1 | ABX00032 | Arduino | Digi-Key | 1050-ABX00032-ND | $27.00 | $8.81
46 | LCD-1602-I2C-V2_FT | U9 | LCD-1602-I2C-V2-FT | 1 | KS0061 | https://www.microcenter.com/product/632704/inland-1602-i2c-lcd-display-module | microcenter.com | 221861 | $4.99 | $0.08
46 |  |  | ⬆alternative | 0 |  |  | Digi-Key | CN0295D |  | $0.41
47 | TXB0106PWR | U11 | TSSOP-16_L5.0-W4.4-P0.65-LS6.4-BL | 1 | TXB0106PWR | TI | LCSC | C38253 | $1.36 | $0.02
48 | AD8065ARTZ-REEL7 | U13 | SOT-23-5_L3.0-W1.7-P0.95-LS2.8-BR | 1 | AD8065ARTZ-REEL7 | ADI(亚德诺)/LINEAR(凌特) | LCSC | C9648 | $3.04 | $0.21
49 | HT7550-1_C16106 | U16 | SOT-89-3_L4.5-W2.5-P1.50-LS4.2-BR | 1 | HT7550-1 | HOLTEK(台湾合泰/盛群) | LCSC | C16106 | $0.13 | $0.08
50 | TP5100_C379389 | U26 | TQFN-16_L4.0-W4.0-P0.65-BL-EP | 1 | TP5100 | Nanjing Extension Microelectronics | LCSC | C379389 | $0.52 | $0.12
51 | LM358ADT | U30 | SOIC-8_L4.9-W3.9-P1.27-LS6.0-BL | 1 | LM358ADT | STMicroelectronics | LCSC | C92457 | $0.12 | $3.04
52 | HY2120-LB | U33 | SOT-23-6_L2.9-W1.6-P0.95-LS2.8-BR | 1 | HY2120-LB | HYCON | LCSC | C168778 | $0.24 | $0.01
53 | HY2213-BB3A | U34,U35 | SOT-23-6_L2.9-W1.6-P0.95-LS2.8-BR | 2 | HY2213-BB3A | HYCON(台湾宏康) | LCSC | C113632 | $0.13 | $0.02
 | Li ion battery (to be bought locally) |  |  | 2 | PRT-12895 |  | Digi-Key |  | $6.60 | $13.20
 | Power supply alternative |  |  | 1 | WR9MD2000CCP-F(R6B) |  | Digi-Key |  | $9.42 | $9.42
 | Power supply |  |  |  | SWH15-9-EB-P5 |  | Digi-Key | 102-SWH15-9-EB-P5-ND
 |  |  |  |  |  |  |  |  | total | $57.05

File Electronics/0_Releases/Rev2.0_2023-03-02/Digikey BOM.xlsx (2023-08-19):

ID | Name | Designator | Footprint | Quantity per PCB | Manufacturer | Supplier | Supplier Part | Price per unit | price per PCB
11 | Nut_M2 | H2,H3,H4,H5 | KEYSTONE_1902C | 4 | Essentra Components | Digi-Key | 04M020040HN | $0.14 | $0.56
12 | Screw_M2_5mm | H6,H7,H8,H9 | KEYSTONE_1902C | 4 | Essentra Components | Digi-Key | 50M020040G004 | $0.14 | $0.56
37 | STUD_M2_15mm | S1,S2,S3,S4 | STANDOFF+SCREW_M2 | 4 | Würth Elektronik | Digi-Key | 971150244 | $0.95 | $3.80
38 | SPACER_M3 | S5,S6,S7,S8 | Board Support Snap Fit | 4 | Würth Elektronik | Digi-Key | 709440800 | $0.23 | $0.92
45 | ARDUINO_NANO_33_IoT | U8 | ARDUINO_NANO_33_IOT | 1 | Arduino | Digi-Key | 1050-ABX00032-ND | $27.00 | $27.00
 | HEF4067BT,653 | U1,U6,U7,U10 |  | 4 |  | Digi-Key |  | $2.05 | $8.20 | $23.49
 | AD8066ARZ-R7 | U2,U29 |  | 2 |  | Digi-Key |  | $7.42 | $14.84 | $117.45
 | PPTC041LFBN-RC | CON4 |  | 1 |  | Digi-Key |  | $0.45 | $0.45 | total cost of this group
 |  |  |  |  |  |  |  | Total | $56.33
 |  |  |  |  | Nuber of PCB ordered | 5 | 2
 |  |  |  |  | Total price | $281.65 | $112.66

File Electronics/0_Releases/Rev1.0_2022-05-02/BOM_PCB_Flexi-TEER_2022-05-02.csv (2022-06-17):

ID | Name | Designator | Footprint | Quantity | Manufacturer Part | Manufacturer | Supplier | Supplier Part | Price
1 | 35pF | C2,C3 | C0603 | 2
2 | 0.1u | C4,C5 | C0603 | 2
3 | 2K | R2,R4 | RES-ADJ-TH_3296W-L | 2 | 3296W-1-202LF | Bochen | LCSC | C118206 | 0.179
4 | 2k | R3,R5 | R0603 | 2
5 | 50 | R6 | R0603 | 1
6 | 300 | R7,R8,R9 | R0603 | 3
7 | 1k | R10 | R0603 | 1
8 | MAX4644EUA+T | U1,U2,U3,U4,U5,U6 | UMAX-8_L3.0-W3.0-P0.65-LS4.9-BL | 6 | MAX4644EUA+T | MAXIM(美信) | LCSC | C2673669 | 2.461
9 | ICL7660SCPAZ | U7 | DIP-8_L9.8-W6.6-P2.54-LS7.6-BL | 1 | ICL7660SCPAZ | Intersil | LCSC | C13725 | 1.357
10 | OP295GPZ | U10 | DIP-8_L9.8-W6.6-P2.54-LS7.6-BL | 1 | OP295GPZ | Analog Devices | LCSC | C208350 | 10.326
11 | ARDUINO_NANO_33_IoT | U9 | ARDUINO_NANO_33_IOT | 1
12 | INA592IDGKR | U11 | VSSOP-8_L3.0-W3.0-P0.65-LS4.9-BL | 1 | INA592IDGKR | TI(德州仪器) | LCSC | C2058638 | 3.018
13 | Adafruit ADS1115 breakout | U12 | ADAFRUIT ADS1115 | 1 | 1085 | Adafruit
14 | REF200AU2K5 | U14 | SOIC8 | 1
15 | ad9833 Module header1x7 | U15 | AD9833 | 1
16 | LM358 | U8 | SOIC-8_L4.9-W3.9-P1.27-LS6.0-BL | 1 | TI | LM358MX/NOPB | LCSC | C16416 | 0.566
17 | Electrode Out | H1 | HDR-F-2.54_1X4 | 1 |  |  | LCSC | C225501 | 0.084
18 | PSU Input | H2 | HDR-F-2.54_1X2 | 1 |  |  | LCSC | C49661 | 0.037
19 | 10uF | C1,C7 | CAP-TH_L4.0-W2.6-P5.00-D0.5 | 2 | K104K15X7RF53H5 | VISHAY(威世) | LCSC | C1620174 | 0.116
20 | 1u | C6 | CAP-D3.0×F1.5 | 1

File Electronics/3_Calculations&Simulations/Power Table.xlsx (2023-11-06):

Rail | Component PN | Description | Datasheet | Qty. | Current per component, mA | Total current, mA | Checked | digital logic voltage
5V | LTC1983ES6-5#TRPBF | Negative -5V generator | Linear Tech (https://www.analog.com/media/en/technical-documentation/data-sheets/1983fc.pdf) | 1 | 0.06 | 0.06 | yes | >1.1 V = HIGH ; <0.3V = LOW
5V | AD8066ARZ-RL | FastFET Op Amps (dual) | Analog Devices (https://www.analog.com/media/en/technical-documentation/data-sheets/AD8065_8066.pdf) | 2 | 14.9 | 29.8 | yes | N/A
5V | AD8065ART-R2 | FastFET Op Amp (single) | Analog Devices (https://www.analog.com/media/en/technical-documentation/data-sheets/AD8065_8066.pdf) | 1 | 8.2 | 8.2 | yes | N/A
5V | LM358ADT | Low-power dual Op Amp | STMicroelectronics (https://www.st.com/content/ccc/resource/technical/document/datasheet/61/46/87/01/98/ed/44/c5/CD00000464.pdf/files/CD00000464.pdf/jcr:content/translations/en.C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) | 1 | 1.2 | 1.2 | yes | N/A
5V | AD8137YCPZ-REEL7 | Differential ADC Driver | Analog Devices (https://www.mouser.pl/datasheet/2/609/AD8137-1502272.pdf) | 1 | 3.6 | 3.6 | yes | >1.7V = HIGH, <0.7V = LOW
5V | 10k resistors |  |  | 1 | 0.5 | 0.5 |  | N/A
5V | 4.7k resistor |  |  | 3 | 1 | 3 |  | N/A
5V | ADS1015IDGSR | I2C 12-Bit ADCs | TI (https://www.ti.com/lit/ds/symlink/ads1013.pdf?HQS=dis-mous-null-mousermode-dsf-pf-null-wwe&ts=1669473269152) | 1 | 0.3 | 0.3 | yes | N/A
5V | HEF4067BT,653 | 16-channel MUX | Nxperia (https://assets.nexperia.com/documents/data-sheet/HEF4067B.pdf) | 4 | 0.3 | 1.2 | yes | >4V = HIGH, <1V = LOW
5V | TXB0106PWR | Level translator | TI (https://www.ti.com/general/docs/suppproductinfo.tsp?distId=10) | 1 | 0.01 | 0.01 | yes | N/A
 |  | LCD backlight |  | 1 | 100 | 100
 |  |  |  |  | total | 147.87

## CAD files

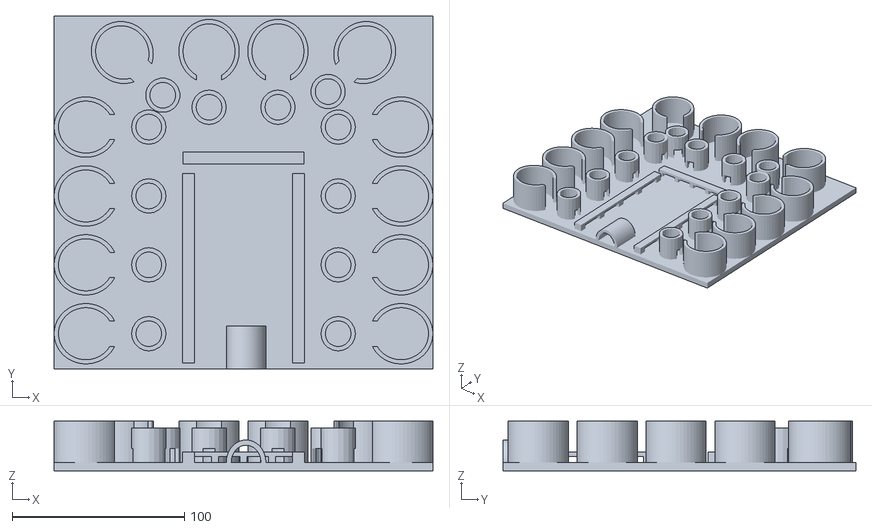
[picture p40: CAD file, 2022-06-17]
Mechanics/models/TEErMainDesignA.stl
220.0 x 205.0 x 29.0

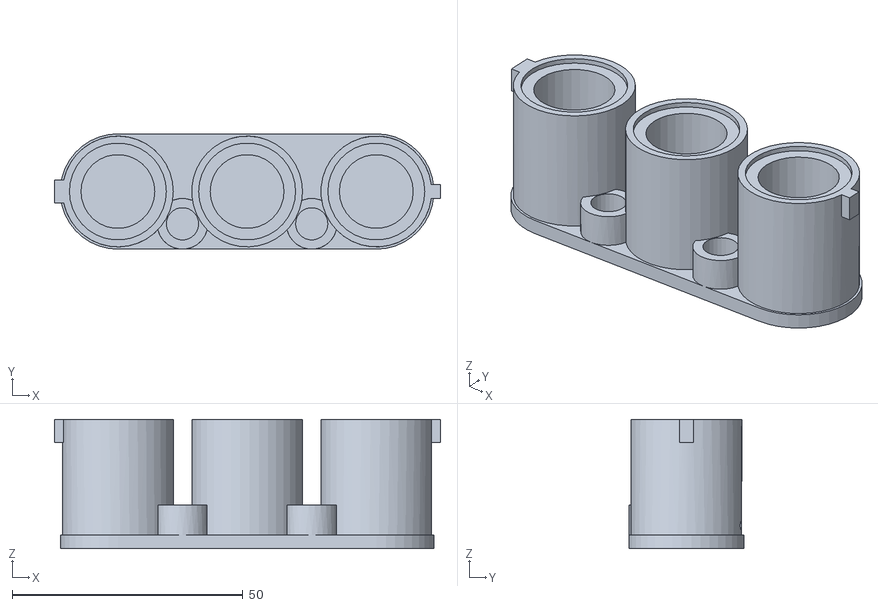
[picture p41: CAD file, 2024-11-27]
3d Models/FlexiTEER case-transwell triplet bottom unit.stl
83.6 x 25.0 x 28.0

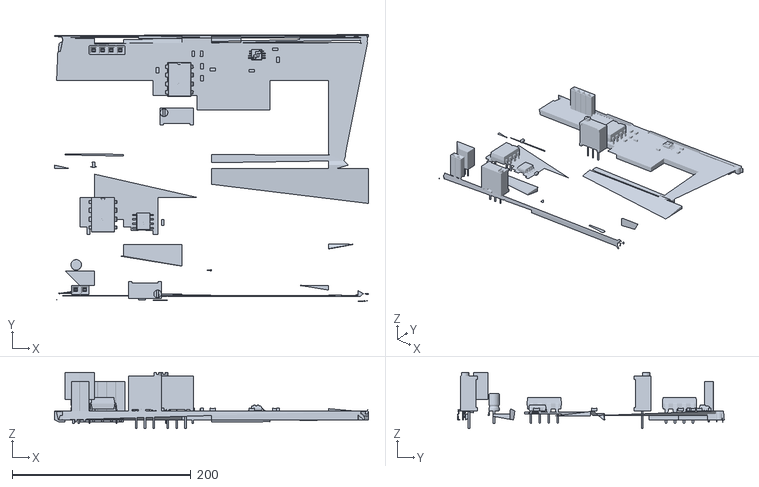
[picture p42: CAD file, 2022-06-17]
Mechanics/models/CustomtranswellTEERchamber001.stl
351.7 x 298.7 x 63.0

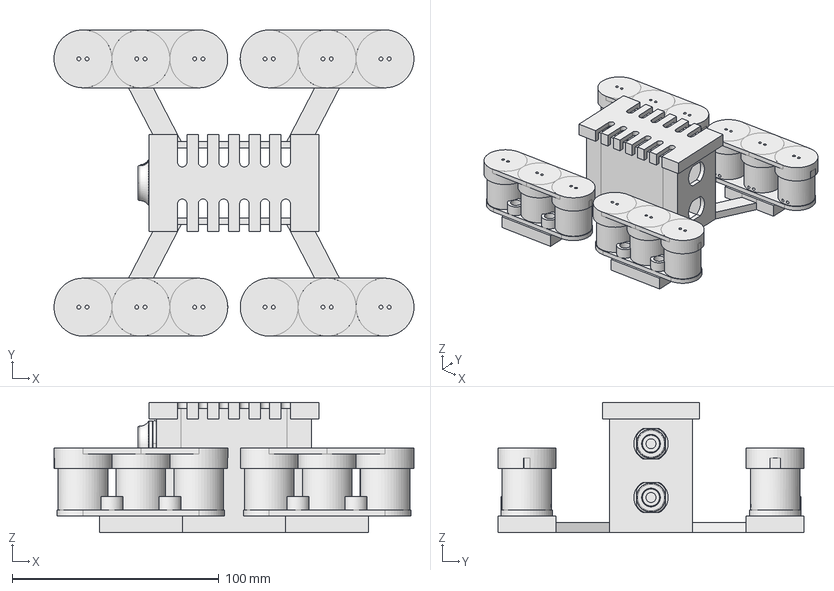
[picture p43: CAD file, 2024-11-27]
3d Models/FlexiTEER case.FCStd
174.0 x 148.0 x 63.0 mm
Base Platform
4 sets of triplet transwells
socket 1
socket 2
lid

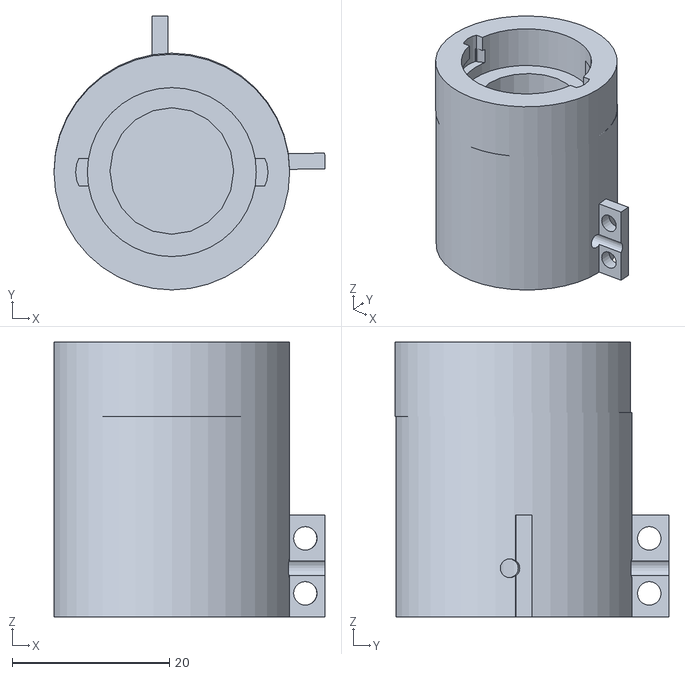
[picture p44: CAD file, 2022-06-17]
Mechanics/models/CustomtranswellTEERchamber002.stl
34.5 x 34.9 x 35.0

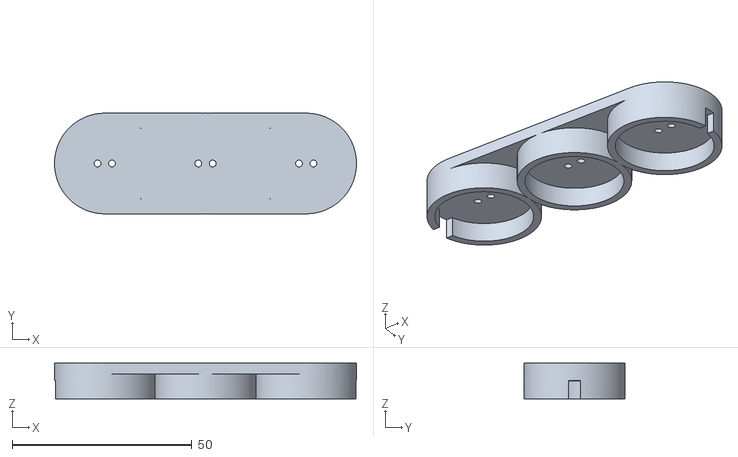
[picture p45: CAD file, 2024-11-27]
3d Models/FlexiTEER case-transwell triplet top unit.stl
84.0 x 28.0 x 10.0

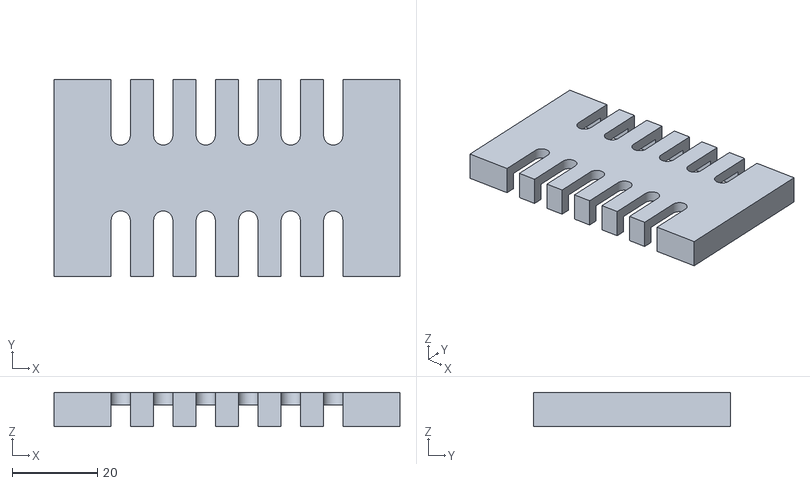
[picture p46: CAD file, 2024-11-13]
3d Models/baseplatform-lid.stl
81.4 x 46.4 x 8.00

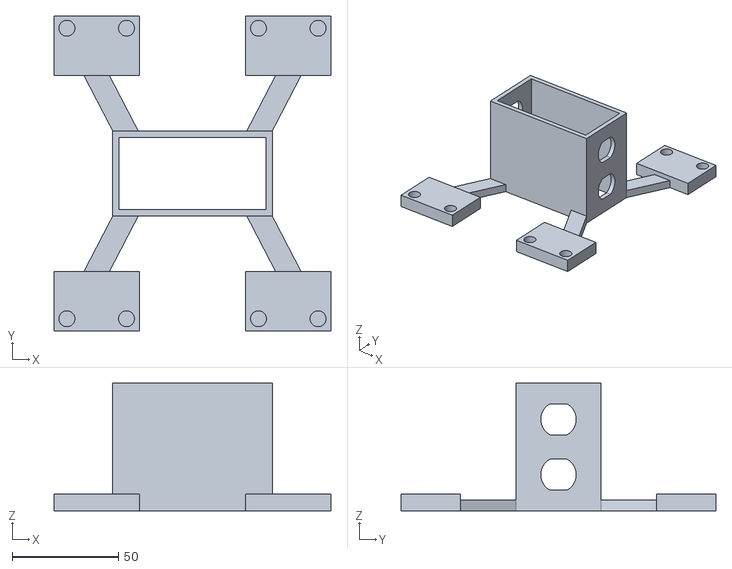
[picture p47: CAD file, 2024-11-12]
3d Models/FlexiTEER case-Base Platform.stl
130.0 x 148.0 x 60.0

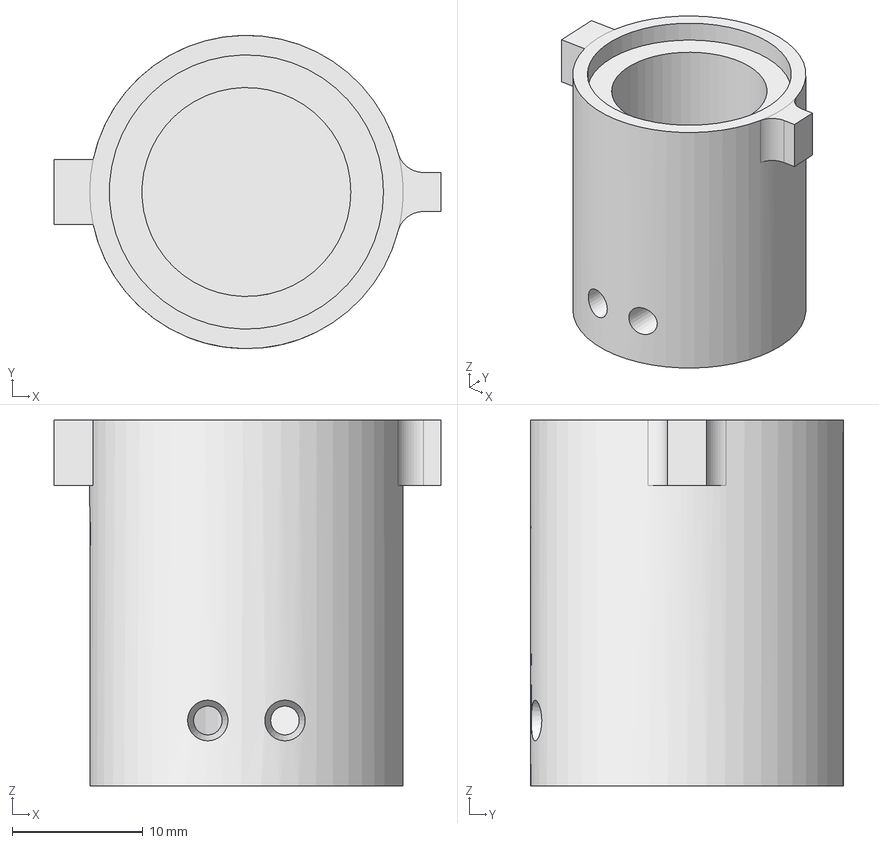
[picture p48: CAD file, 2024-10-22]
3d Models/transwell_self_sealing.FCStd
29.6 x 24.0 x 28.0 mm

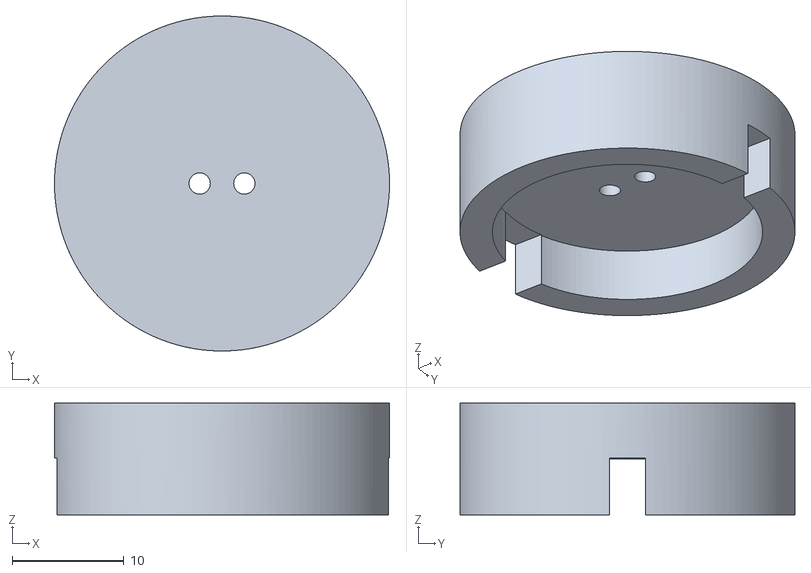
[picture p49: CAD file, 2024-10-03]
3d Models/FlexiTEER case-transwell top.stl
30.0 x 30.0 x 10.0

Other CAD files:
3d Models/FlexiTEER case-transwell Bottom Unit self seal.stl
3d Models/FlexiTEER case-transwell Bottom Unit.stl

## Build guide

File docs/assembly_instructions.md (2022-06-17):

[10uF SMD Capacitor]:Parts.yaml#capacitor603
[35pF SMD Capacitor]:Parts.yaml#capacitor603
[0.1uF SMD Capacitor]:Parts.yaml#capacitor603
[2k SMD Resistor]:Parts.yaml#resistor603
[50 SMD Resistor]:Parts.yaml#resistor603
[300 SMD Resistor]:Parts.yaml#resistor603
[1k SMD Resistor]:Parts.yaml#resistor603
[SPDT Switch]:Parts.yaml#MAX4644EUAT
[ICL7660 Chargepump]:Parts.yaml#ICL7660SCPAZ
[Arduino Nano]:Parts.yaml#Arduino
[OP295 OP Amp]:Parts.yaml#OP295GPZ
[INA592 Diff Amp]:Parts.yaml#INA592IDGKR
[ADS1115 Breakout]:Parts.yaml#ADS1115
[REF200 Current Source]:Parts.yaml#REF200AU2K5
[ad9833 Function Generator]:Parts.yaml#AD9833
[LM358 OP Amp]:Parts.yaml#LM358
[Curved Soldering Iron Tip]:Parts.yaml#Curved_Solder_Iron_Tip
[Straight Soldering Iron Tip]:Parts.yaml#Straight_Solder_Iron_Tip
[16x1 Female Pin Header]:Parts.yaml#Female_pin_header
[7x1 Female Pin Header]:Parts.yaml#Female_pin_header
[10x1 Female Pin Header]:Parts.yaml#Female_pin_header
[0.5mm Solder Wire]:Parts.yaml#0.5mm_solder
[0.3mm Solder Wire]:Parts.yaml#0.3mm_solder
[Wire Snips]:Parts.yaml#wire_snips
[Solder Sucker]:Parts.yaml#solder_sucker
[Soldering Iron]:Parts.yaml#Soldering_Iron
[Grabber Tool]:Parts.yaml#Grabber

# Assembly Instructions

{{BOM}}

## Step 1: Order PCB

1. Download the [Gerber File](files/Gerber_PCB_Flexi-TEER.zip), [BOM](files/BOM_PCB_Flexi-TEER_2022-05-02.csv) and [Pick and Place File](files/PickAndPlace_PCB_Flexi-TEER_2022-05-02.csv) for the PCB.
* Sign into account or create an account if new.
* Go to [JLCPCB Website](https://cart.jlcpcb.com/quote?edaOrderUrl=https%3A%2F%2Feasyeda.com%2Forder&electropolishingOnlyNo=no&achieveDate=72 ) website and upload Gerber zip folder. 
* While on the page, drag and drop Gerber zip folder into area that asks for it. In the example image, I also used the SMT assembly service by selecting it.
*  Upload **BOM** and **Pick and Place** .csv files. Select electronics and hobbies/developmental board for the description. 
* Select parts that you desire to be soldered onto the board for you via the SMT assembly service.

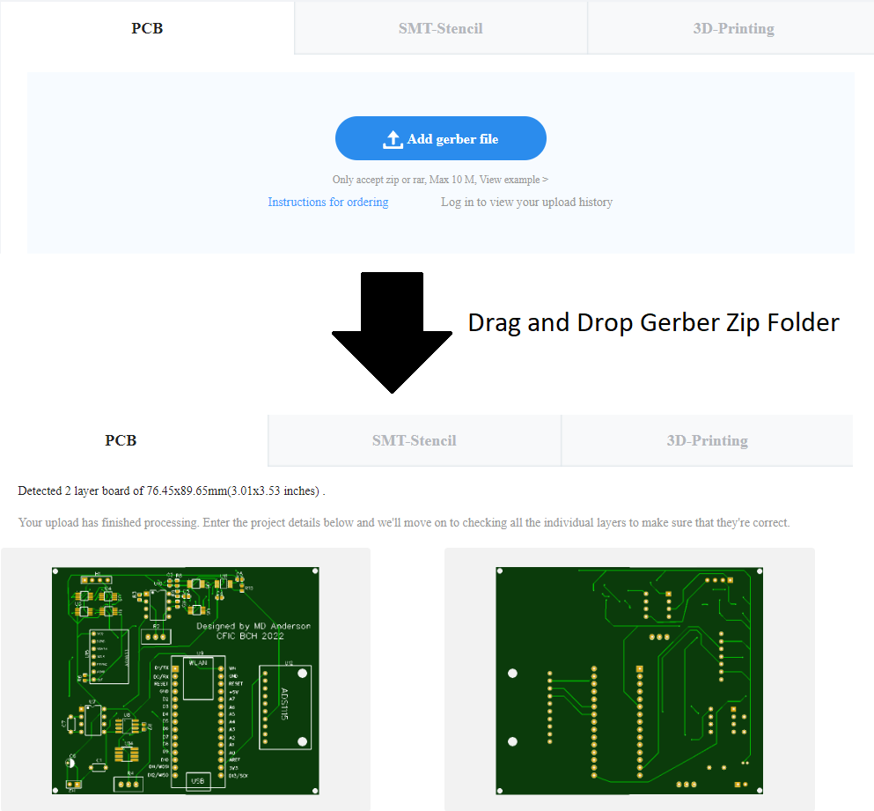
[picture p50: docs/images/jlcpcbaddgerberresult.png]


>i **Note**
>i SMT Assembly service is an affordable service where certain components are soldered to the board for you. Not every current component is compatible with this service. I recommend using this as its time consuming to solder these very tiny components. 

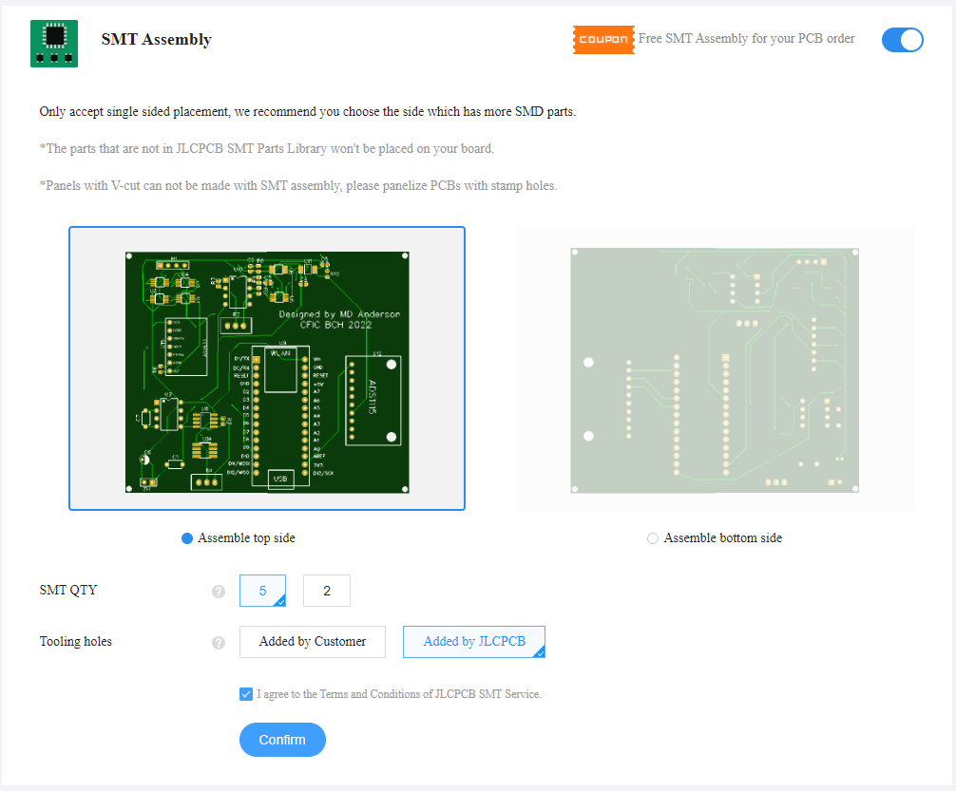
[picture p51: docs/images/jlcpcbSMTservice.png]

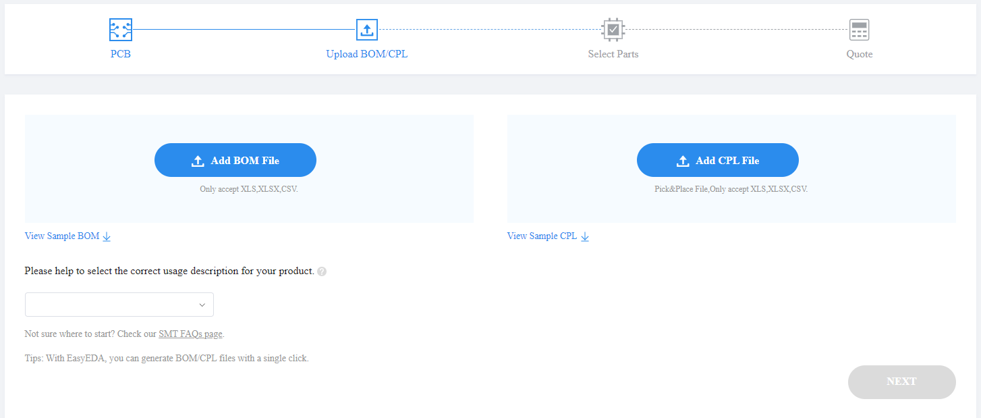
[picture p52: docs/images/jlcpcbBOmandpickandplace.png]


## Step 2: Order Components

1. Go to [mouser project](https://www.mouser.com/ProjectManager/ProjectDetail.aspx?AccessID=c21611a5ee) and order integrated circuit (IC) components. 
* Order remaining generic parts such as 603 footprint resistors and capacitors. 

>i **Note**
>i If you used the SMT assembly service, you do not need to order those parts again. 

>i **Note**
>i Not all parts make sense to order individually. I recommend ordering the 603 footprint resistors and capacitors as part of variety book set. 

## Step 3: Solder Surface Mount Components (SMD)
Solder components onto circuit board in the order below with a [Soldering Iron]{Qty:1, cat: tool}. A strategy that has worked well with small chips is to use a soldering iron with very fine 0.3mm solder. First place some solder onto each pad for the component, then place component with [Grabber Tool]{Qty:1, cat: tool} and press into place with tweezers and gently touch each lead from the component with the soldering iron until the solder melts around it. 

>i **Note**
>i a [Curved Soldering Iron Tip]{Qty: 1, cat: tool} will help solder SMD components to board.

>i **Note**
>i If you used the SMT service, some of these parts may already be installed. 

1. [10uF SMD Capacitor]{Qty: 2}
* [35pF SMD Capacitor]{Qty: 2}
* [0.1uF SMD Capacitor]{Qty: 2}
* [2k SMD Resistor]{Qty: 2}
* [50 SMD Resistor]{Qty: 1}
* [300 SMD Resistor]{Qty: 3}
* [1k SMD Resistor]{Qty: 1}
* [SPDT Switch]{Qty: 6}
* [INA592 Diff Amp]{Qty: 1}
* [REF200 Current Source]{Qty: 1}
* [LM358 OP Amp]{Qty: 1}

## Step 4: Solder Through Hole Components

>i **Note**
>i a [Straight Soldering Iron Tip]{Qty: 1, Cat: tool} will help solder through hole components to board.

1. 2x [16x1 Female Pin Header]{Qty: 2}, one for each side of Arduino Nano IOT
2. 1x [7x1 Female Pin Header]{Qty: 1} in ad9833 socket
3. 1x [10x1 Female Pin Header]{Qty: 1} in ADS1115 socket

## Step 4: Solder Male Pin Headers
If ordered any breakout boards (ADS1115, AD9833, Arduino, etc.), solder male pin headers to each board.

## Step 5: Attach Breakout Boards
Attach each breakout board and Arduino into respective sockets.

## Step 6: Flash Arduino Sketch
Currently no sketch is available.

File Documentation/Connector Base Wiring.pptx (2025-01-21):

## Connector Base Wiring

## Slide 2

- RJ45 patch cables are T568B convention

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
Souriau-Sunbank by Eaton
JMX series 12 conductor plug pinout

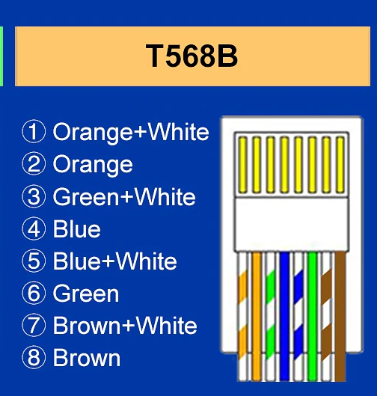
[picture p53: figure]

V2 V1 I2 I1

- G/stripe = V2
- Blue = V1
- Blue/stripe = I2
- Green = I1

## QC

1. Verified every single connection to not only be isolated, but also connected to its appropriate wire (2x)
2. Placed labels on each wire to say which chamber it is and which wire
3. Accidentally cut one RJ45 off and reattached and confirmed connection. Blue might be shaky though
4. Exposed 2-3mm of silver on each electrode for bleach treatment to make into AgCl electrodes
5. 2-3 Ohms is average resistance measured between electrode and RJ45 terminal

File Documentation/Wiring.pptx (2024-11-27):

## Wiring

## Autoclavable Connection

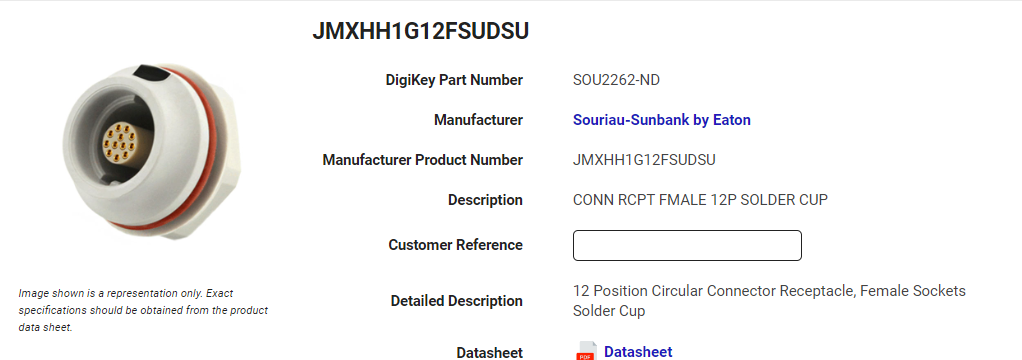
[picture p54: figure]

- 12 wire pins
- 28 gauge wire at lowest (so largest size)
- Chart below for max cable diameter for the given sealing gland

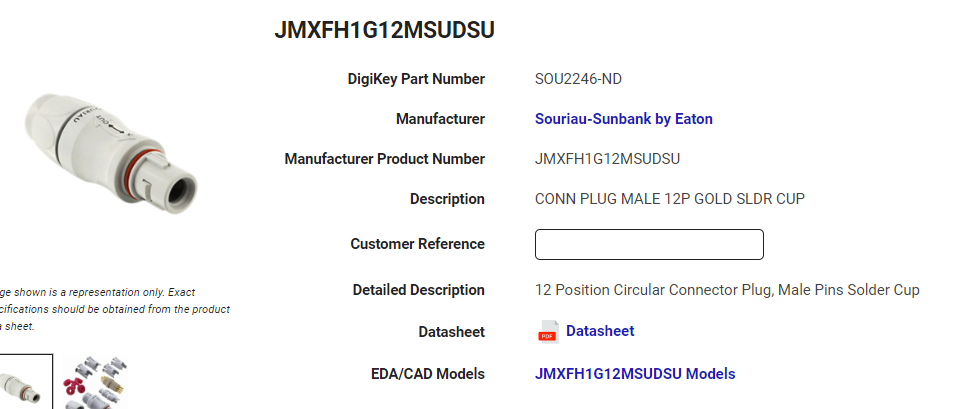
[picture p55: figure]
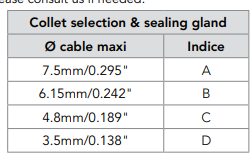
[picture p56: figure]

## 12 wire cable

- Need 12 wire 28gauge cable with max diameter of 7.5mm

https://www.mouser.com/ProductDetail/Alpha-Wire/M1612-SL005?qs=ng8%252BTWoKejlTQNkxlWY9%2FQ%3D%3D

- Need 28 AWG RJ45 cables to splice into above cable

https://amz.run/9l8O

- Need splice between original 28 gauge cable and ethernet connected one
  - https://amz.run/9l8R

- Need splice between 28AWG electrode and 28 AWG wire
  - https://amz.run/9l8o

Need electrode 28 AWG
https://amz.run/9l95

- Need thin solder for cup terminals
  - https://amz.run/9lq2

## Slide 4

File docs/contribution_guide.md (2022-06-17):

# Contribute to Flexi-TEER

## Mission
We are creating a powerful and flexible TEER measurement device that will affordably enable new experiments to be conducted in a user friendly way. 

## Welcome

Welcome everyone! My name is Michael Anderson (I sometimes use MD Anderson as my name online as Michael Anderson is wayyy too common of a name). I am currently a PhD level staff scientist in microscopy core at Boston Children's Hospital. My background is in physics and microscopy/optics. 

This Flexi-TEER project has been a side project of mine for the past couple years. For the first year it was just an idea that TEER seems simple and it shouldn't be very hard to make a new device to enable us to conduct an experiment we wanted to do. The second year was realizing that it is more difficult and nuanced than it seemed at first. We also realized that this device has a ton of potential, much more than just our individual lab. So we decided to make it Open-Source in hopes that this project could be expanded on and really have a large impact. We have made massive progress though and I think we are very close to having an actual functioning device. 

**Point people to your Code of Conduct for the project, and require users to read it before they go any further** (Need to make Code of Conduct)

# How Can I Contribute?

Below is a breakdown of aspects of the project and what we are currently working on

* **[.](hardware.md){step}** (This explains all hardware)
* **[.](Accessories.md){step}** (This explains current accessories)

**List Communication Channels: (Jira, Slack)**

**Tell readers how to submit changes: This is the process for adding your work or changes to the repository or collection of ongoing work** What should this be? No good ideas. 

You can report any bugs to our [github](https://github.com/mdanderson03/Flexi-TEER)
Tell readers how to report a bug: 
**Ask your contributors to stay on the lookout for can any potential issue that might cause problems for the project. These could be problems in code , content omissions or copy errors, or any issues with the functionality or design of your project. Basically, by asking users to report bugs, you’re asking for feedback on work that’s been done.** (dont know quite how to do this yet).

Most projects invite all contributors to tell the project lead about bugs, so “debugging” or fixing problems happens quickly and with the input of the community. Take a look at Atom’s example for how to teach people to report bugs to your project.

Tell developers about your recognition model - Remember, you need to acknowledge value of the time and work your volunteers give your project. Here, provide a pre-emptive “thank you” for interest contributing. 
# Recognition

This is an important aspect, especially so in the open-source space. We recognize you in several different ways:

1. On a list on the website homepage
* In specific sections of the detailed work. For example, if you added on a hardware module, I will directly credit you for it. 
* We will publish scientific papers. If you contribute in a way that is meaningful for an experiment, then you will be cited as a co-author or placed in the acknowledgment on that paper. 
  
List any recognition contributors might receive for participating in your project. You can also outline how contributors can “level up” to become project maintainers (a certain number of bugs resolved, a certain number of changes or contributions successfully submitted to the project). 

You can leave this blank for now, and fill it in later.
Let developers know where to go for help - provide clear contact info, and outline the process for getting in touch, for anyone with questions.

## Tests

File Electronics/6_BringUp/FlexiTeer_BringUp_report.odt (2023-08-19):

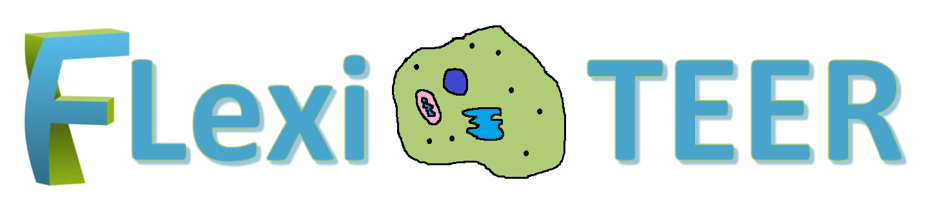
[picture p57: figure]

Document | Bring up report
Project | Flexi Teer
PCB | Rev2.0
PCB SN | #1...#5
Authors | MD Anderson, Dennis Yaskevich
Date | ongoing
Version | ongoing

## 1. Orientation

### 1.1 What is the purpose of this document

This document describes the initial bring up (verification) testing of the FlexiTeer rev.2 hardware. All of test performed and the issues detected during the testing must be reflected in this document.

### 1.2 Who should read this document

This is deeply technical document more inclined to electronics design. It mainly useful for the engineer who is designing the second revision of hardware to see at glance all of the issues the previous revision had.

### 1.3 Requisite documents

Table below contains the relevant design documentation and it’s current versions as of writing of this document.

Document name | Link to the document | Latest updated on
Schematic_Flexi-TEER_2023-02-18.pdf | GitHub (https://github.com/mdanderson03/Flexi-TEER/blob/main/documents/Schematic/Schematic_Flexi-TEER_2023-02-18.pdf) | 2023-02-18
PCB Layout | oshwlab.com (https://oshwlab.com/md.anderson03/flexi-teer) | 2023-02-18

### 1.4 Test environments

Currently 2 people are working on the project.

Test environment | Test engineer | Equipment available | Test to be performed
Boston Children Hospital | MD Anderson | To be completed | Shorts and resistance measurement
Hackerspace Krakow | Dennis Yaskevich | USB Microscope NB-MIKR-300 | Visual inspection Shorts and resistance measurement

## 2. Basic hardware testing

### 2.1 Visual inspection

Test equipment:

        - USB Microscope NB-MIKR-300

To be completed by Dennis

### 2.2 Shorts and resistance measurement

Test equipment:

  - Multimeter

Resistance measurement to be performed on to powered off unit according to the table below.

Signal name | Meas. point | Expected value | Actual value | Status
Q33_6 | BT6 vs GND | >1k | Over Load | OK
Q3_2 | BT5 vs BT6 | >1k | 12.3M Ohms | OK
Q3_2 | BT5 vs GND | >1k | 15.2M Ohms | OK
VBAT | BT3 vs BT6 | >1k | 14M Ohms | OK
VBAT | BT3 vs GND | >1k | 82k Ohms | OK
VIN | Left side of R1 vs GND | >1k | Overload | OK
+5V | TP31 vs GND | >1k | 8.16k Ohms | OK
+3V3 | TP30 vs GND | >1k | 8.55k Ohms | OK
-5V | TP29 vs GND | >1k | 230k Ohms | OK

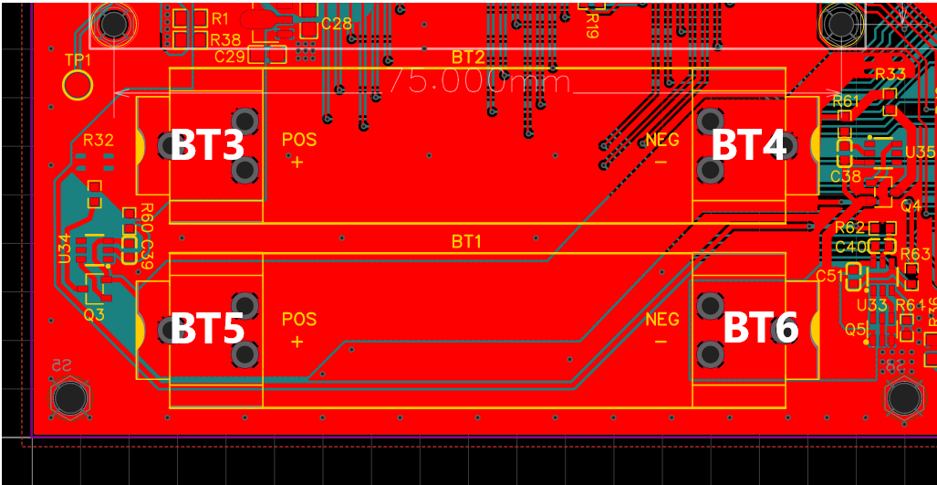
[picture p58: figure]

## 2.3 Power up and voltage measurement

Test equipment:

  - Multimeter
  - lab power supply / 9V wall adapter

Issue E1 is detected when inserting the batteries. To be investigated by DY

Suggested temporary solution: Solder shorting 0 Ohm resistors R1 and R38. Wire can be soldered instead of this resistors. Apply 9V input power to the CON1 with 100mA current limit if possible.

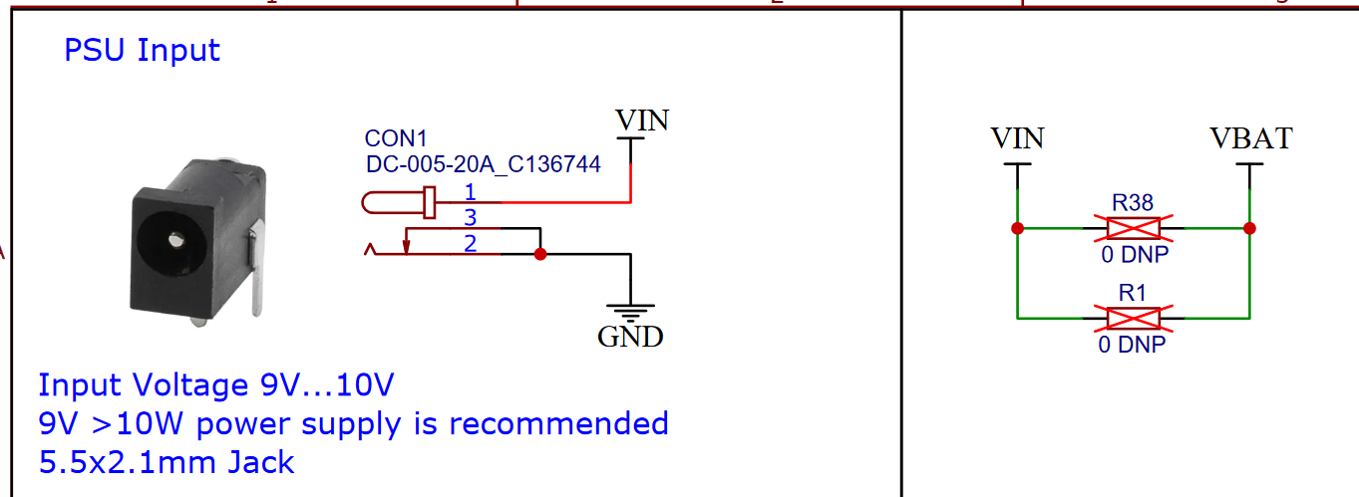
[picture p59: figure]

If no overcurrent / smoke is detected after the power is applied, measure the following voltages:

Rail name | Meas. point | Expected value, V | | | Ref. | Actual value | Status
| | Min. | Nom. | Max.
VIN | R1 vs GND | 8 | 9 | 10 | | 9.01 | OK
+5V | TP31 vs GND | 4.5 | 5 | 5.5 | | 4.98 | OK
+3V3 | TP30 vs GND | 3.0 | 3.3 | 3.5 | | 3.26 | OK
-5V | TP29 vs GND | -5.5 | -5 | -4.5 | | -4.8 | OK
+1V65 | TP27 vs GND | | 1.65 | | | 1.62 | OK
+2V5 | TP25 vs GND | | 2.5 | | | 2.48 | OK

Set status as OK if measured voltage is within the expected values range.

Bilevel Converter Module

Evaluating BiLevel converter and transform to make signals go between -5 and 5 volts to toggle MUX ICs.

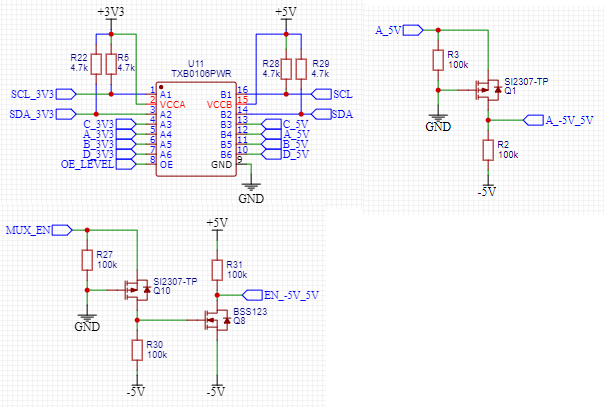
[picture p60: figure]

Rail name | Meas. point | Expected value, V | | | Ref. | Actual value | Status
| | Min. | Nom. | Max.
A in | A_3V3 vs GND | | 3.3 | | | 3.34 | Ok
A shifted | A_5V vs GND | | 5 | | | 4.37 | Ok
A -5_5 | A_-5V_5V vs GND | | -5 and 5 | | | -4.75 and +4.35 | Ok
MUX in | MUX_EN vs GND | | 3.3
MUX_EN -5_5 | EN_-5V_5V vs GND | | -5 and 5
OE enb | OE_LEVEL vs GND | | 3.3 | | | 2.77 | High enough to work, but odd its so low.

Everything appears to be functional with this module.

MUX

Resistance Measurements
Meas. point | Expected Value, Ω | Measured Value | A | B | C | D | Status
Y0 vs Z | 0 | 0 | LOW | LOW | LOW | LOW | Ok
Y1 vs Z | Over Load | Over Load | LOW | LOW | LOW | LOW | Ok
Y4 vs Z | 0 | 0 | LOW | LOW | HIGH | LOW | Ok
Y10 vs Z | Over Load | Over Load | LOW | LOW | HIGH | LOW | Ok

MUX enable, a,b,c,d pins appear to function properly. Channels are switching to proper channels given A,B,C,D logic inputs.

AC Generation

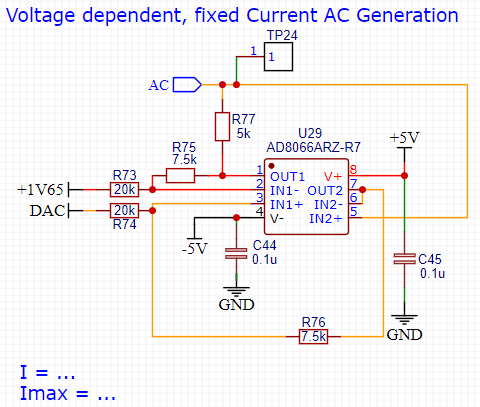
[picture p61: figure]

Test Number | Meas. point | Expected value, V | | | DAC | Actual value | Status
| | Min. | Nom. | Max.
1 | TP24 vs GND | | 0.533 | | 2.24 | .550 | Ok
2 | TP24 vs GND | | -0.583 | | 0.994 | -0.580 | Ok

Arduino defaults to 8bit for DAC. Hardware is 10bit so I added in a code line to make it 10bit input. I put a 12k resistor in as a sub for ‘cell load’ and ran it at around 12Hz (the target frequency) and it worked very well. I believe this module is functioning very well and super close to simulation predictions. Here is a conversion chart between DAC and the ADC on pins A0 and A2 respectively.

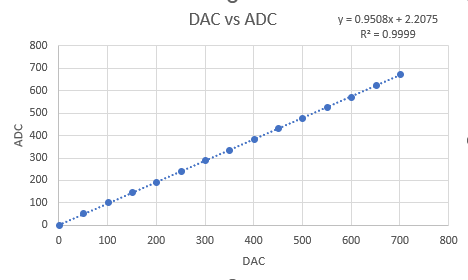
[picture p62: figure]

Here is proof I generated a symmetric AC wave through the 12k resistor. Looks great! (values of 426 and 626 were used as 1.62V (the ref voltage) was projected to be 526).

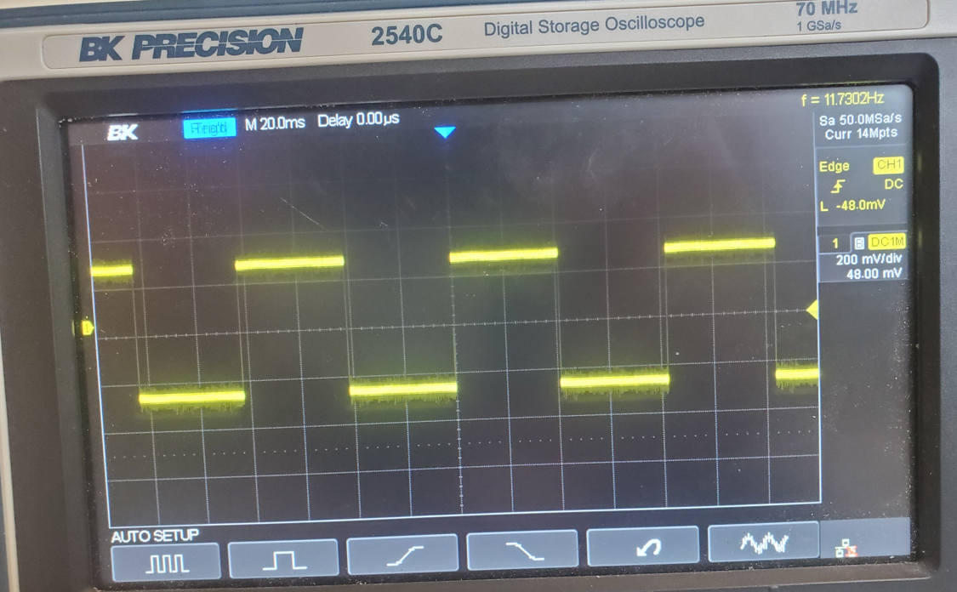
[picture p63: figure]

## Summary

### Assembly issues

No | Issue description | Date/Author | Status

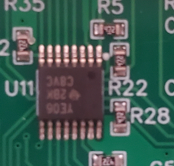
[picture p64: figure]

A1 | Low humming coming from bilevel converter. Some outputs (C and A) stuck at 2.3V no matter what 3V3 corresponding input is. | 15.08.23 MD Anderson | Swapped to different board and noise was not present and bilevel converter worked properly. Pin 13 looked not soldered properly. Measuring this pin removes the noise. ---------- Manual touch up to be applied to pin 13
A2

### Electronics issues

No | Issue description | Date/Author | Status

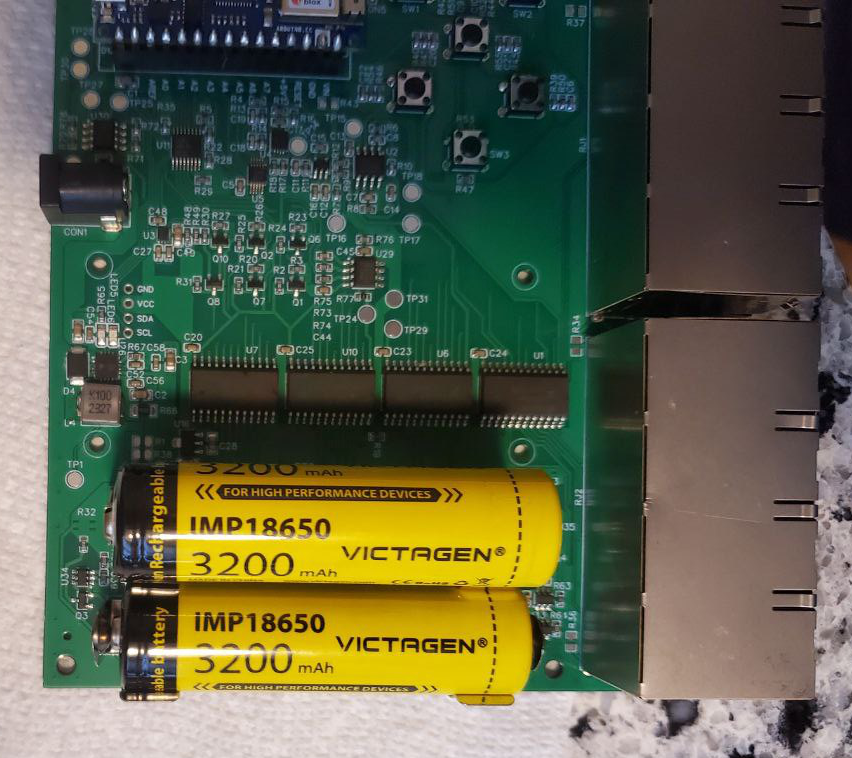
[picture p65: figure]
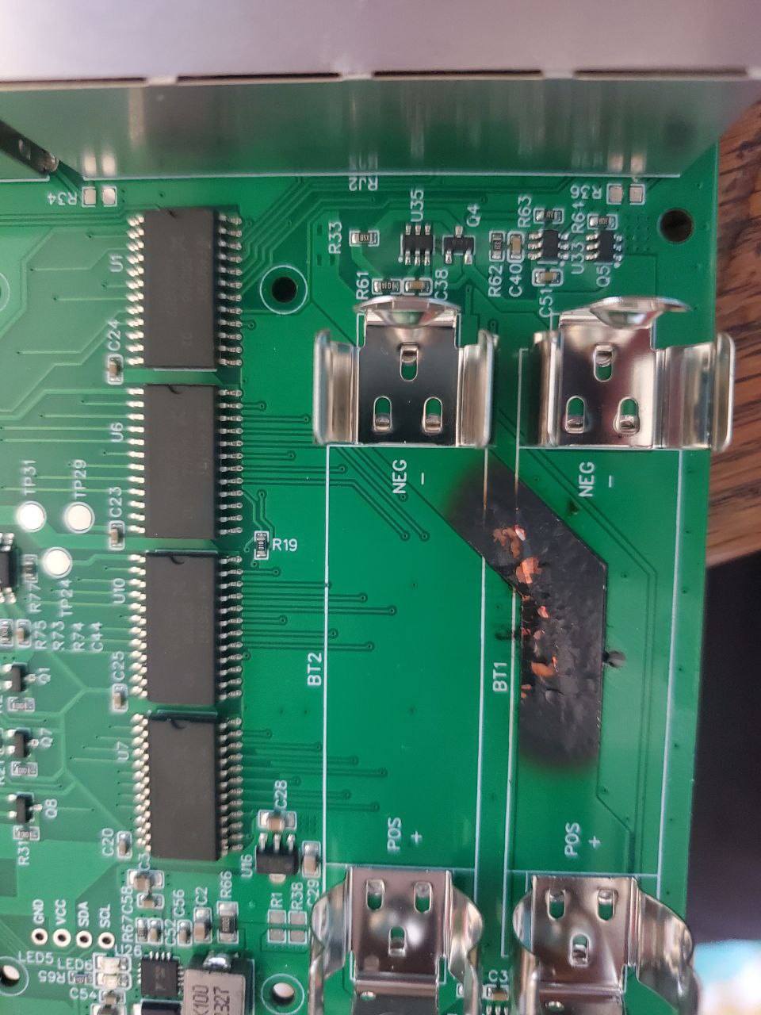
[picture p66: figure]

E1 | After inserting the second battery the PCB trace starts burning | 02.08.23 MD Anderson | When the battery is inserted the battery holder jaws move to the sides, and this causes shorting of the bottom battery -------- Spacing to be increased in the future PCB revision --------- Quick and dirty solution – insert insulator between the battery holders
E2 | L4 inductance to be increased to 22uH. Eval board and old datasheet has this value. L4 MDA7030-100M (C2847485) → MDA7030-220M (C2847487). Pin to pin replacement | 16.08.23 DY | I will use on the samples the value that I will find. For future documentation 22uH will be used.


E3 | Need to take away aref as the pin for the D_3V3 pin. Even though documentation says it can be a GPIO, it is unclear how to do it. Its easier to modify and use one premapped for that usage. This pin is not included in the Arduino GPIO library and it can only be used by initializing it on the registers level: Source (https://forum.arduino.cc/t/how-to-use-arduino-nano-33-iot-aref-pin-for-gpio/933363/2) Schematic (https://docs.arduino.cc/static/585de29d610bc9ea5d7eed9433526b7f/ABX00027-schematics.pdf) | 15.08.23 MD Anderson | Should be updated in next prototype: we can apply permanent pull up to PD signal, and route the MUX controll signal to A7 pin of the arduino. Another option is pull up enable pin on bilevel converter. -------- For now I would attempt to use this pin at the register level. If it turns out to be too complex, then manual rework and sap to A7 pin would be a solution
E4

Hardware verification report

There is going to be the license information Currently the project documentation is provided as is 10 of 10

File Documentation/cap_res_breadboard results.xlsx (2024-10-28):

Capacitence (uF) | Resistance (Ohms) (10k standard) | Resistance (Ohms) (690 standard)
0 | 10000 | 690
0.1 | 10000 | 690
0.47 | 9990 | 689
1 | 9661 | 689
2.2 | 8142 | 689
4.7
10 |  | 687

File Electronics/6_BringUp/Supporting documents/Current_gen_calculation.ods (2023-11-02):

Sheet: Defining the range
Vout | 4.5000000000000003e-005 | 1.0000000000000001e-005 | -1.0000000000000001e-005 | -4.5000000000000003e-005
50000 | 2.25 | 0.5 | -0.5 | -2.25
10000 | 0.45000000000000001 | 0.10000000000000001 | -0.10000000000000001 | -0.45000000000000001
1000 | 4.5000000000000005e-002 | 1.e-002 | -1.e-002 | -4.5000000000000005e-002
500 | 2.2500000000000003e-002 | 5.0000000000000001e-003 | -5.0000000000000001e-003 | -2.2500000000000003e-002
100 | 4.5000000000000005e-003 | 1.e-003 | -1.e-003 | -4.5000000000000005e-003
1 | 4.5000000000000003e-005 | 1.0000000000000001e-005 | -1.0000000000000001e-005 | -4.5000000000000003e-005
 | Output voltage range = 5V … 10uV … -10uV … -5V
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

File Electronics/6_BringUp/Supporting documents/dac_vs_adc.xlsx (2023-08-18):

DAC Value | ADC Value trial 1 | Voltage
1 | 1 | 0.00322265625
51 | 51 | 0.1643554687
101 | 100 | 0.322265625
151 | 147 | 0.4737304687
201 | 193 | 0.6219726562
251 | 241 | 0.7766601562
301 | 289 | 0.9313476562
351 | 335 | 1.079589844
401 | 384 | 1.2375
451 | 432 | 1.3921875
501 | 478 | 1.540429687
551 | 526 | 1.695117187
601 | 568 | 1.83046875
651 | 622 | 2.004492187
701 | 672 | 2.165625
751 | 708 | 2.281640625
801 | 708 | 2.281640625
851 | 708 | 2.281640625
901 | 708 | 2.281640625
951 | 708 | 2.281640625
1001 | 708 | 2.281640625

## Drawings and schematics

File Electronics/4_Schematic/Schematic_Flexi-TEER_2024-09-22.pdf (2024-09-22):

A | A
B | B
C | C
D | D

TITLE:
Sheet_1 | REV: 2.1
Date: | 2023-08-23

Sheet: 1/7
Drawn By: MD Anderson

Company: Boston Children's Hospital

V2.0 July 2022. Contributed by Dennis Yaskevich, Michael Anderson and Jose Yesta Lozano

# Schematic Revision History

V2.1 August 2023 Contributed by Dennis Yaskevich and Michael Anderson

1. Replace TXB0106PWR with TXS0102DQMR that supports open drain for i2c usage.
2. Changed R18 resistor to be between TP14 and junction between pin 8 on AD8137 and R17
3. Eliminated PD pin on arduino pin A7 as its not needed. Pin is designed to float on AD8137 in on state (verify float feature)
4. Moved d_pin from aref to A7 on arduino due to issues in using aref as a GPIO pin

V2.1 Changes

5. Added 0.1uF bypass capacitors on bilevel translator per data sheet
6. Changed L4 inductance from 10uH to 22uH (BOM updated)
7. Connected CS from TP5100 to A0 on MCU. Pulled up with 10k to 3V3. (BOM updated)
8. Added in MRA4003T3G diode to pwr in for MCU to prevent MCU from powering board when only connected to computer
9. Eliminated Standby pin connection to MCU from the TP5100 IC
10. Adding in external I2C interfaced DAC IC (MCP4725A0T-E/CH). Tied A0 pin to Vss (GND) pin.
11. Added in separate LDO voltage regulator (AP2204K-ADJTRG1) to only pwr negative rail charge pump.
12. Added pullup resistor (10k Ohms) to enable pin for charge pump IC (LM27761DSGR).
13. Added 220Ohm load to -5 rail line for LM27761DSG IC (charge pump U3)
14. Added in 1M Ohm pull down resistors for V1 and V2 inputs for U2 op amp.

Page name:
Change log

Mux ABCD lines converted to discrete level translation ala previous version mux enable pin.

15. 5V LDO replaced with MIC5209 with enable pin feature
16. U30 OpAmp is replaced with an alternative with single circuit. 1.65V rail is not used anymore
17. Block diagram updated to reflect architectural changes

All resistors are 1% tolerance unless otherwise noted

NOTES

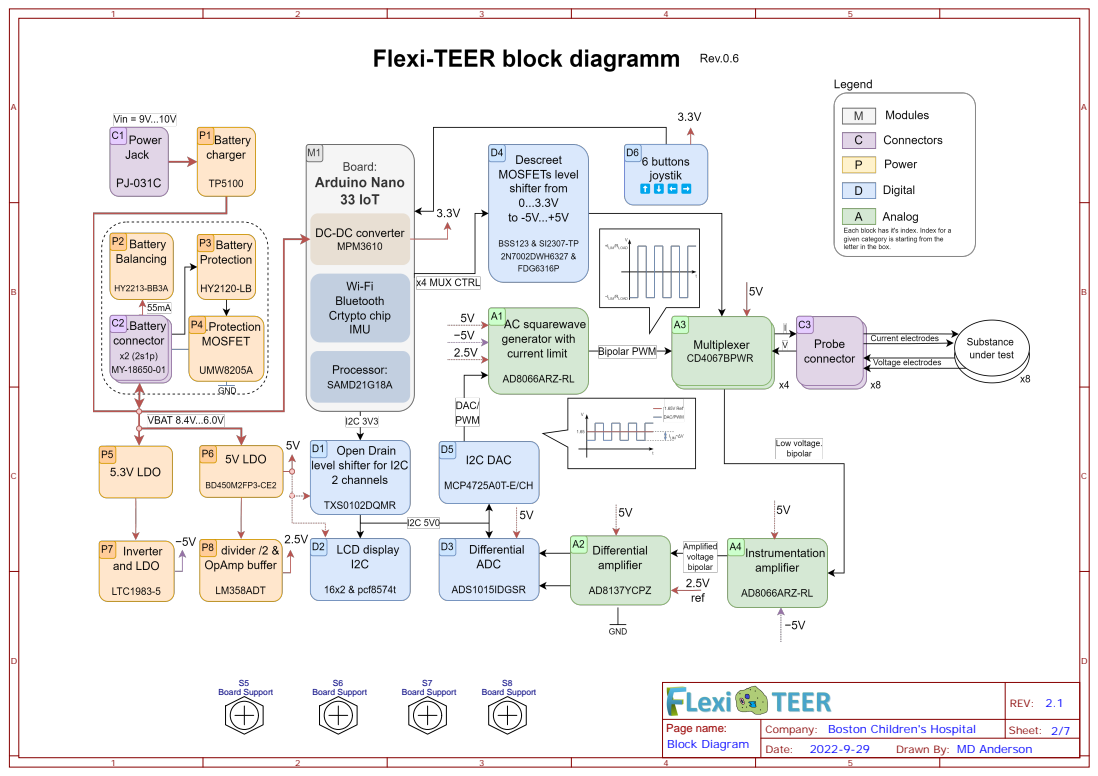
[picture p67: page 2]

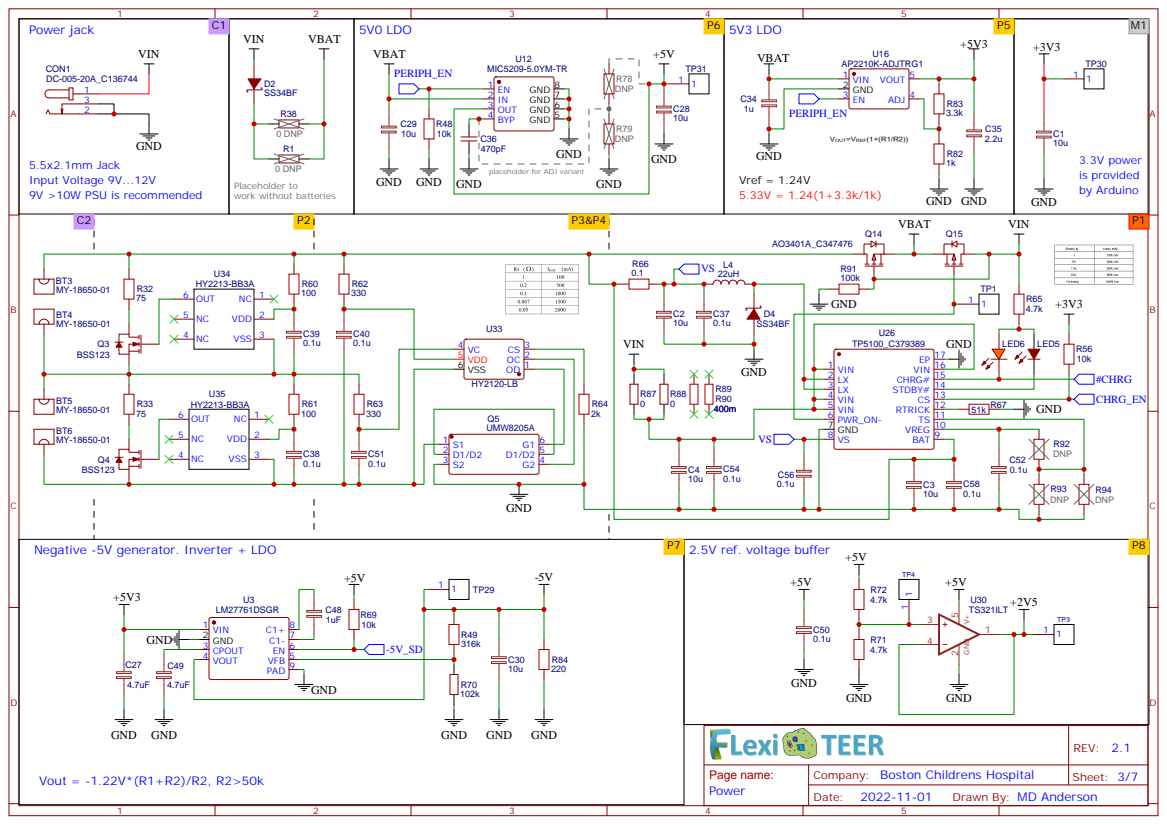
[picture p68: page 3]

placeholder for ADJ variant
GND

VREG 10 TS 11 RTRICK 12 CS 13 STDBY# 14 CHRG# 15 VIN 16 EP 17

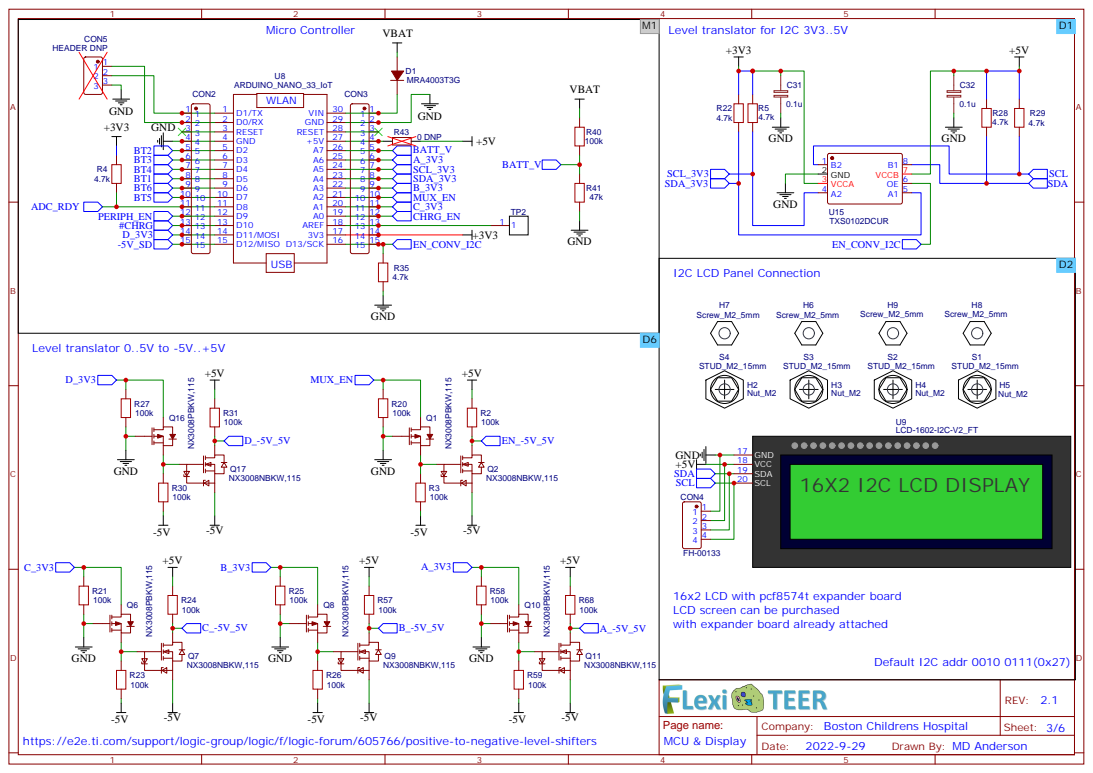
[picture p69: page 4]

16x2 LCD with pcf8574t expander board
LCD screen can be purchased
with expander board already attached

Company: Boston Childrens Hospital

https://e2e.ti.com/support/logic-group/logic/f/logic-forum/605766/positive-to-negative-level-shifters

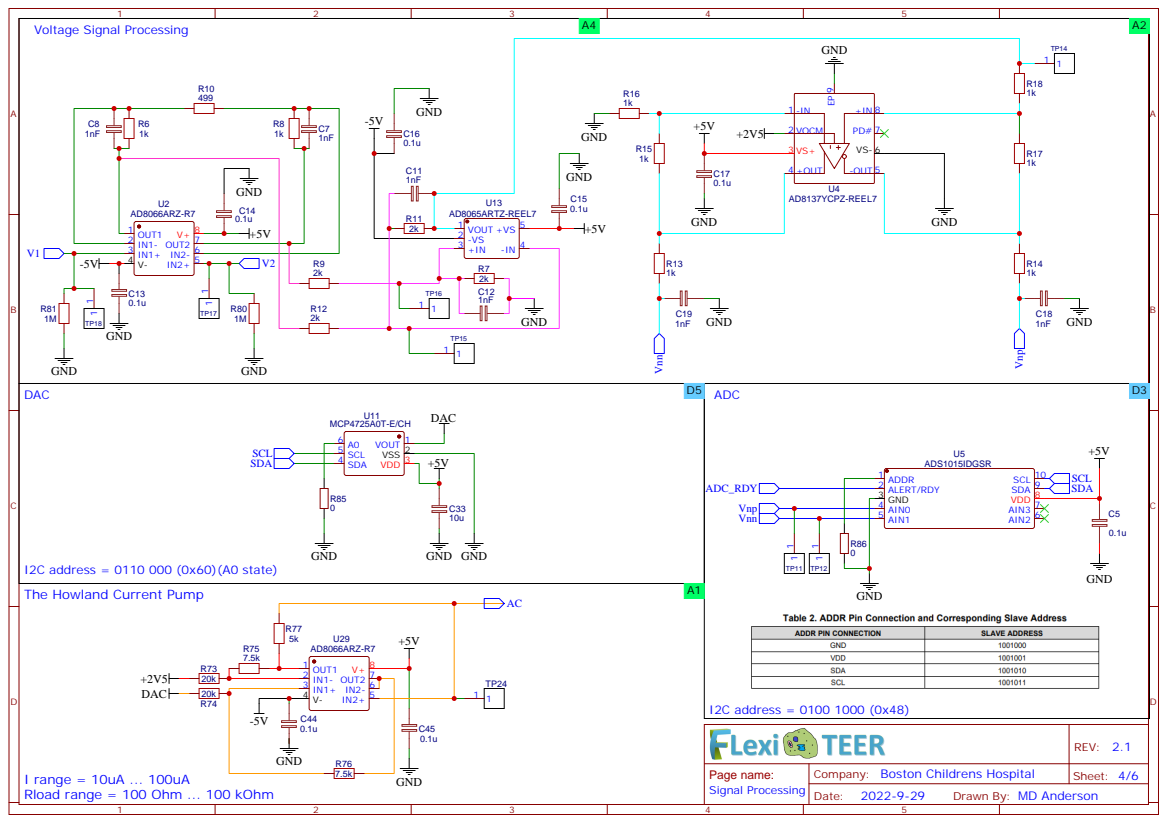
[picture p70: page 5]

I2C address = 0110 000 (0x60)(A0 state)
The Howland Current Pump

Company: Boston Childrens Hospital

I range = 10uA ... 100uA
Rload range = 100 Ohm ... 100 kOhm

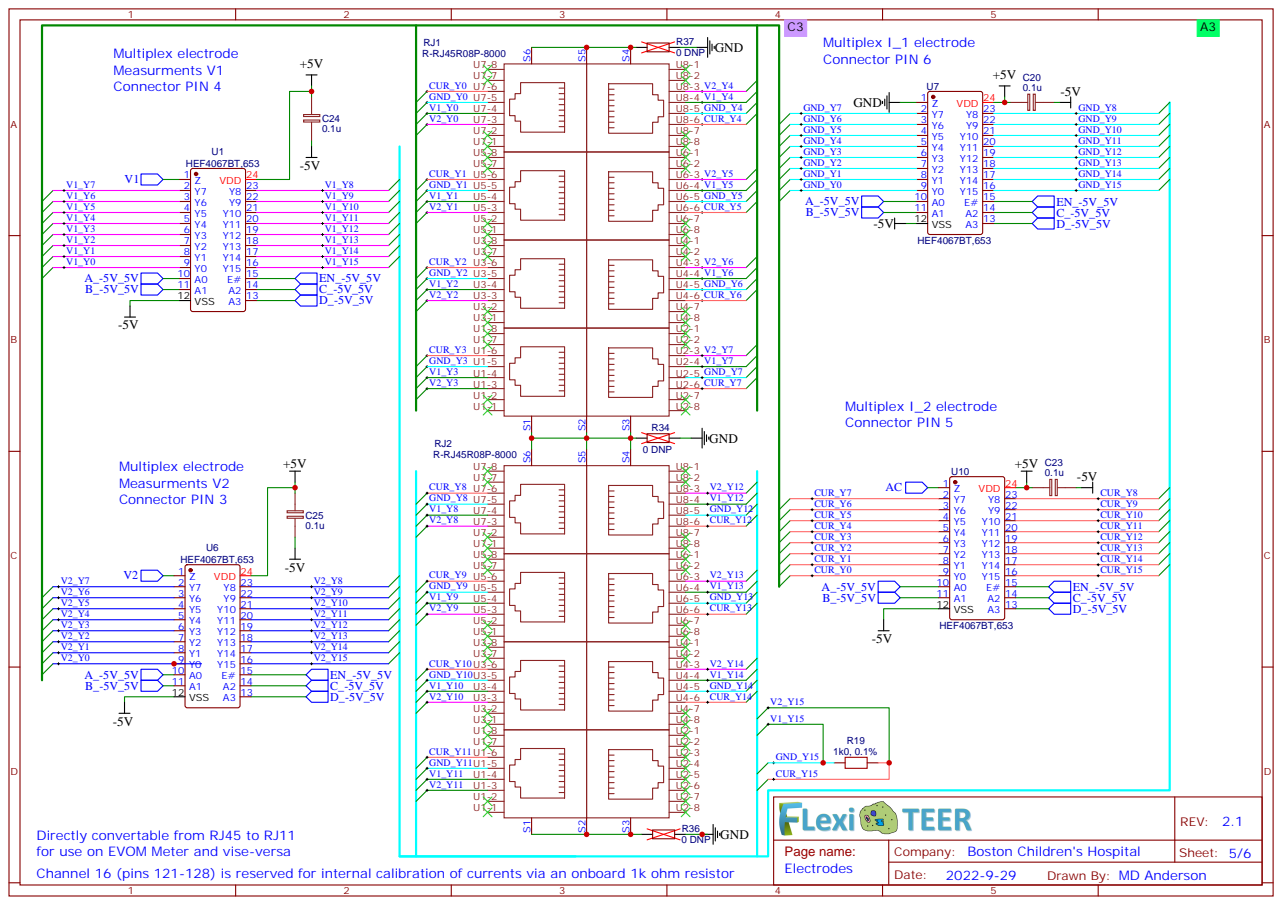
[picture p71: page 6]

Directly convertable from RJ45 to RJ11
for use on EVOM Meter and vise-versa
Channel 16 (pins 121-128) is reserved for internal calibration of currents via an onboard 1k ohm resistor

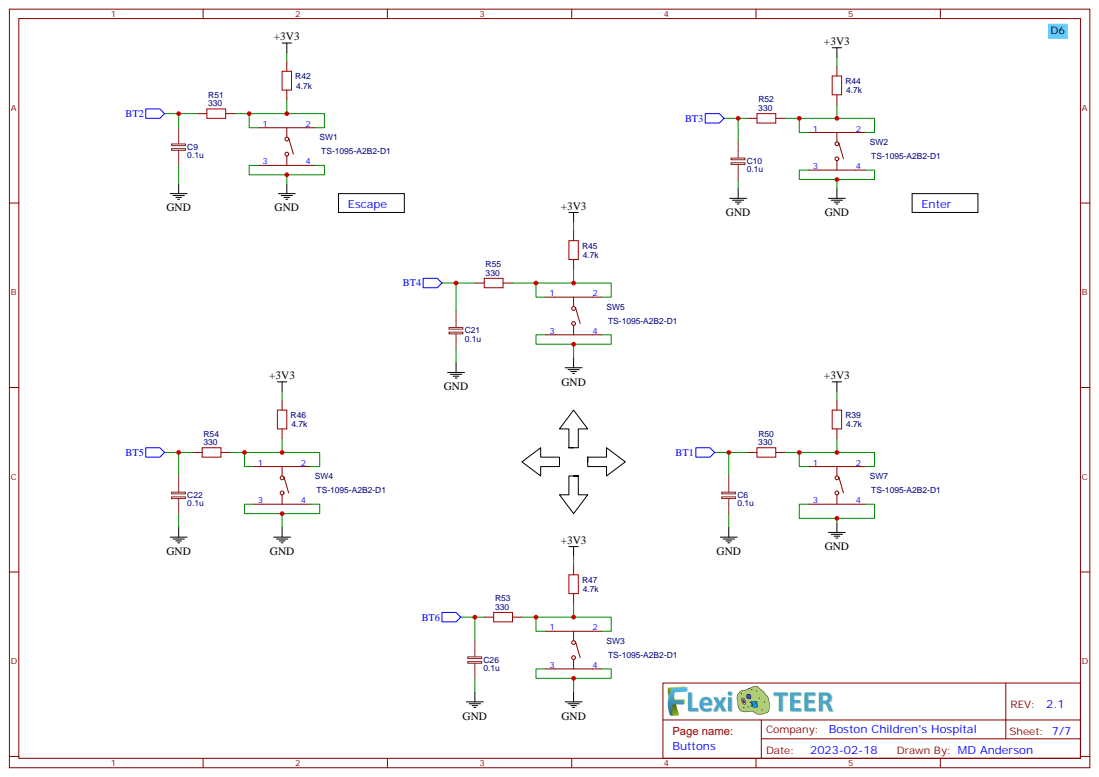
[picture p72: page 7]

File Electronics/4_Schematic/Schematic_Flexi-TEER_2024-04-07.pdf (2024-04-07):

A | A
B | B
C | C
D | D

TITLE:
Sheet_1 | REV: 2.1
Date: | 2023-08-23

Sheet: 1/7
Drawn By: MD Anderson

Company: Boston Children's Hospital

V2.0 July 2022. Contributed by Dennis Yaskevich, Michael Anderson and Jose Yesta Lozano

# Schematic Revision History

V2.1 August 2023 Contributed by Dennis Yaskevich and Michael Anderson

1. Replace TXB0106PWR with TXS0102DQMR that supports open drain for i2c usage.
2. Changed R18 resistor to be between TP14 and junction between pin 8 on AD8137 and R17
3. Eliminated PD pin on arduino pin A7 as its not needed. Pin is designed to float on AD8137 in on state (verify float feature)
4. Moved d_pin from aref to A7 on arduino due to issues in using aref as a GPIO pin

V2.1 Changes

5. Added 0.1uF bypass capacitors on bilevel translator per data sheet
6. Changed L4 inductance from 10uH to 22uH (BOM updated)
7. Connected CS from TP5100 to A0 on MCU. Pulled up with 10k to 3V3. (BOM updated)
8. Added in MRA4003T3G diode to pwr in for MCU to prevent MCU from powering board when only connected to computer
9. Eliminated Standby pin connection to MCU from the TP5100 IC
10. Adding in external I2C interfaced DAC IC (MCP4725A0T-E/CH). Tied A0 pin to Vss (GND) pin.
11. Added in separate LDO voltage regulator (AP2204K-ADJTRG1) to only pwr negative rail charge pump.
12. Added pullup resistor (10k Ohms) to enable pin for charge pump IC (LM27761DSGR).
13. Added 220Ohm load to -5 rail line for LM27761DSG IC (charge pump U3)
14. Added in 1M Ohm pull down resistors for V1 and V2 inputs for U2 op amp.

Page name:
Change log

Mux ABCD lines converted to discrete level translation ala previous version mux enable pin.

15. 5V LDO replaced with MIC5209 with enable pin feature
16. U30 OpAmp is replaced with an alternative with single circuit. 1.65V rail is not used anymore
17. Block diagram updated to reflect architectural changes

All resistors are 1% tolerance unless otherwise noted

NOTES


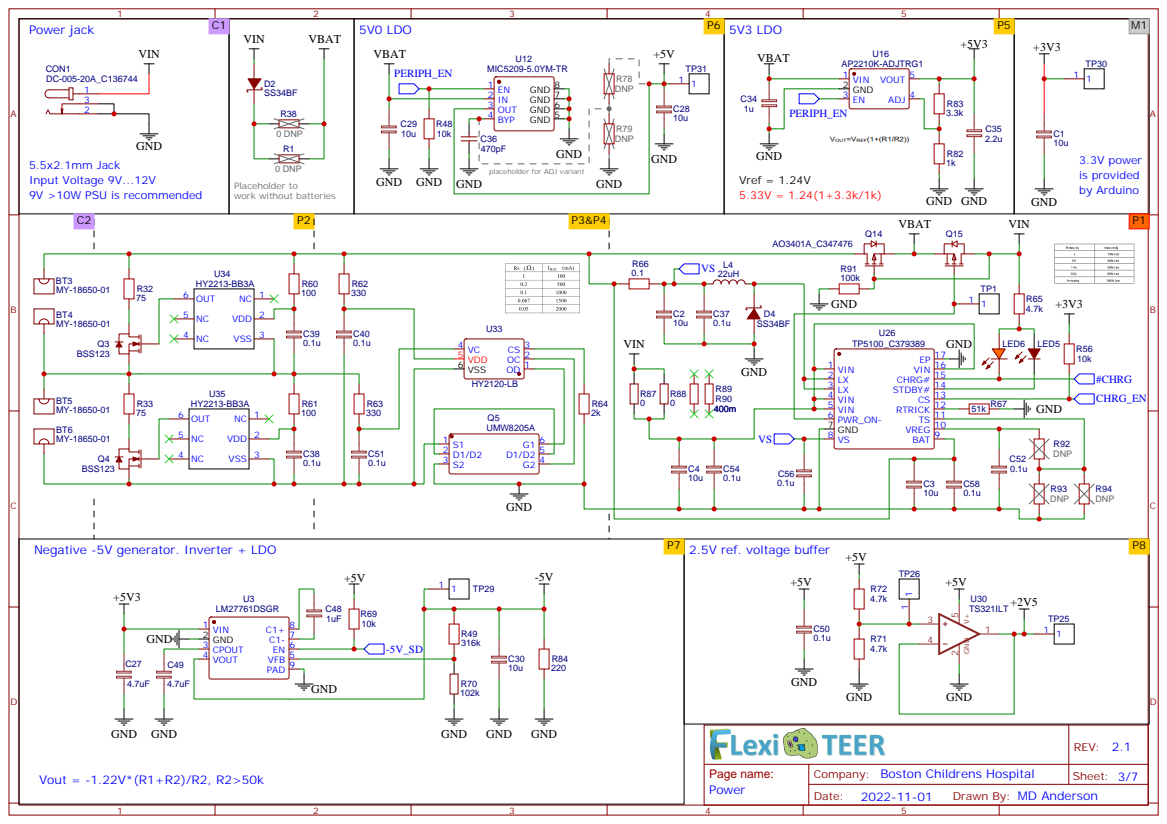
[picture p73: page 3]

placeholder for ADJ variant
GND

VREG 10 TS 11 RTRICK 12 CS 13 STDBY# 14 CHRG# 15 VIN 16 EP 17

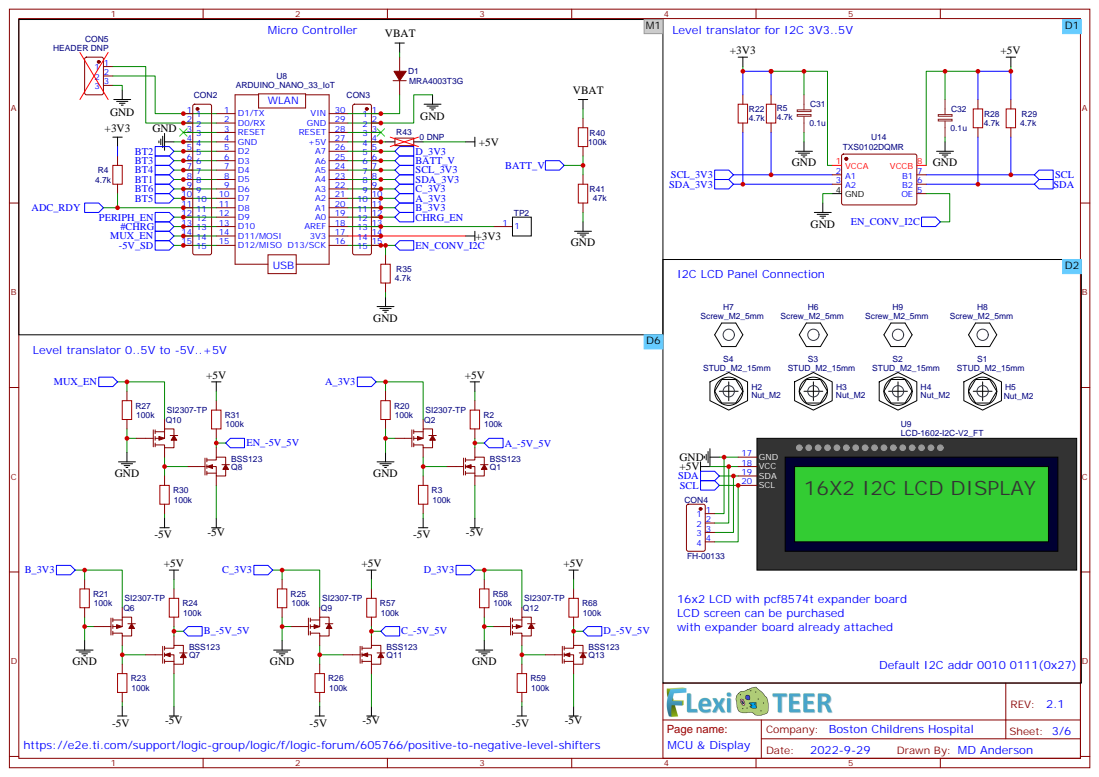
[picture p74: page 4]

16x2 LCD with pcf8574t expander board
LCD screen can be purchased
with expander board already attached

Company: Boston Childrens Hospital

https://e2e.ti.com/support/logic-group/logic/f/logic-forum/605766/positive-to-negative-level-shifters


I2C address = 0110 000 (0x60)(A0 state)
The Howland Current Pump

Company: Boston Childrens Hospital

I range = 10uA ... 100uA
Rload range = 100 Ohm ... 100 kOhm


Directly convertable from RJ45 to RJ11
for use on EVOM Meter and vise-versa
Channel 16 (pins 121-128) is reserved for internal calibration of currents via an onboard 1k ohm resistor


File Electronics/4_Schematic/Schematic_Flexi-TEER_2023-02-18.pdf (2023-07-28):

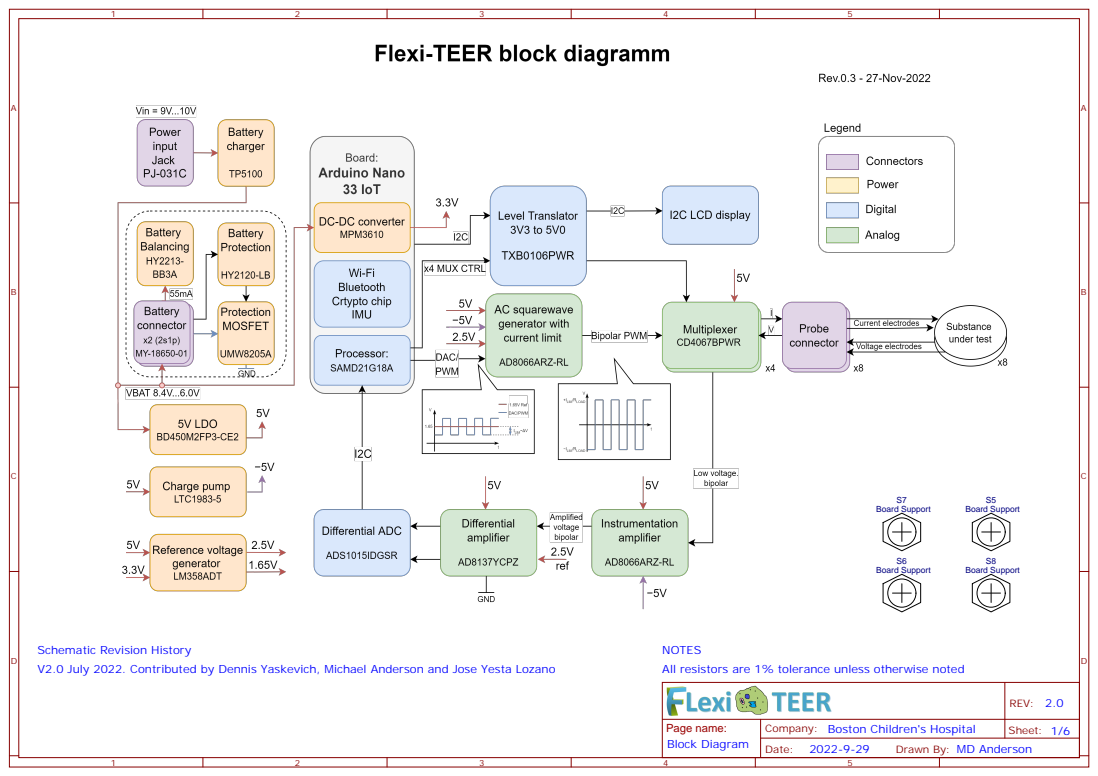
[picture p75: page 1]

Company: Boston Children's Hospital

Drawn By: MD Anderson

## is provided

## Input Voltage 9V...10V

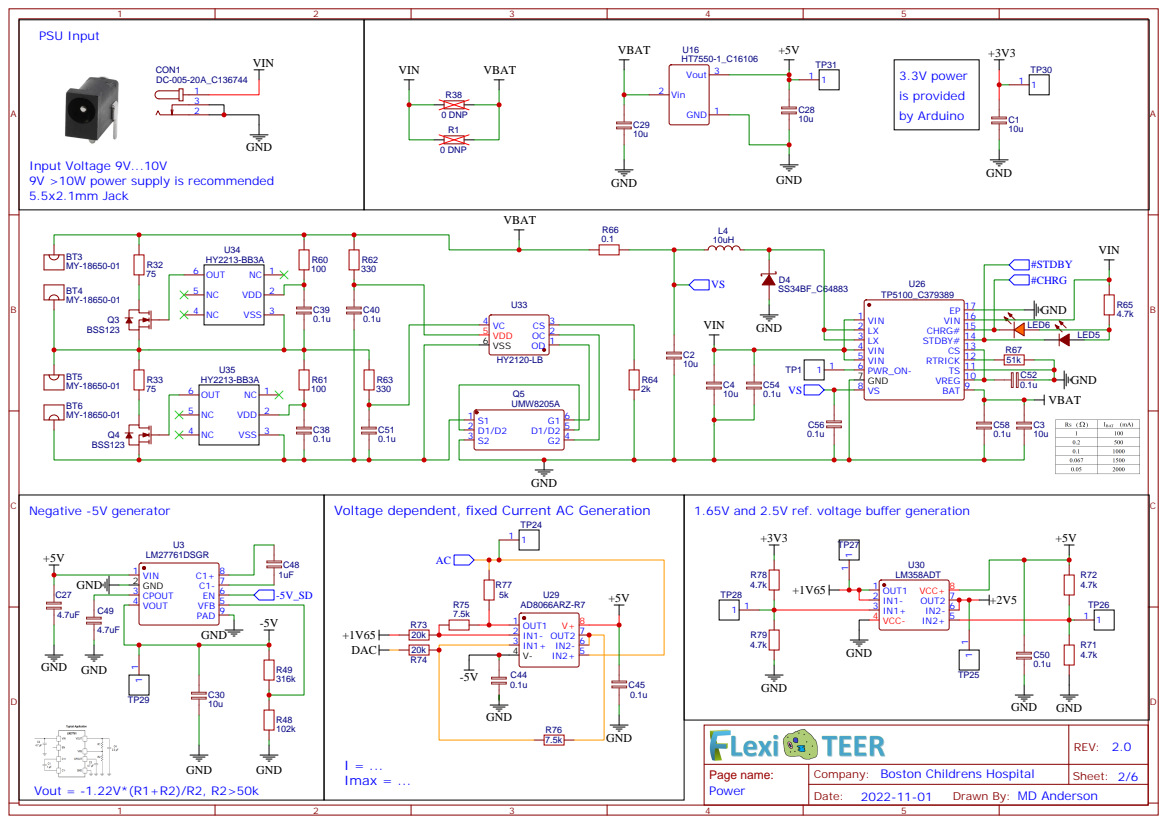
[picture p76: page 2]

9V >10W power supply is recommended
5.5x2.1mm Jack

VREG 10 TS 11 RTRICK 12 CS 13 STDBY# 14 CHRG# 15 VIN 16 EP 17

Voltage dependent, fixed Current AC Generation

## Micro Controller Level translator 3V3..5V

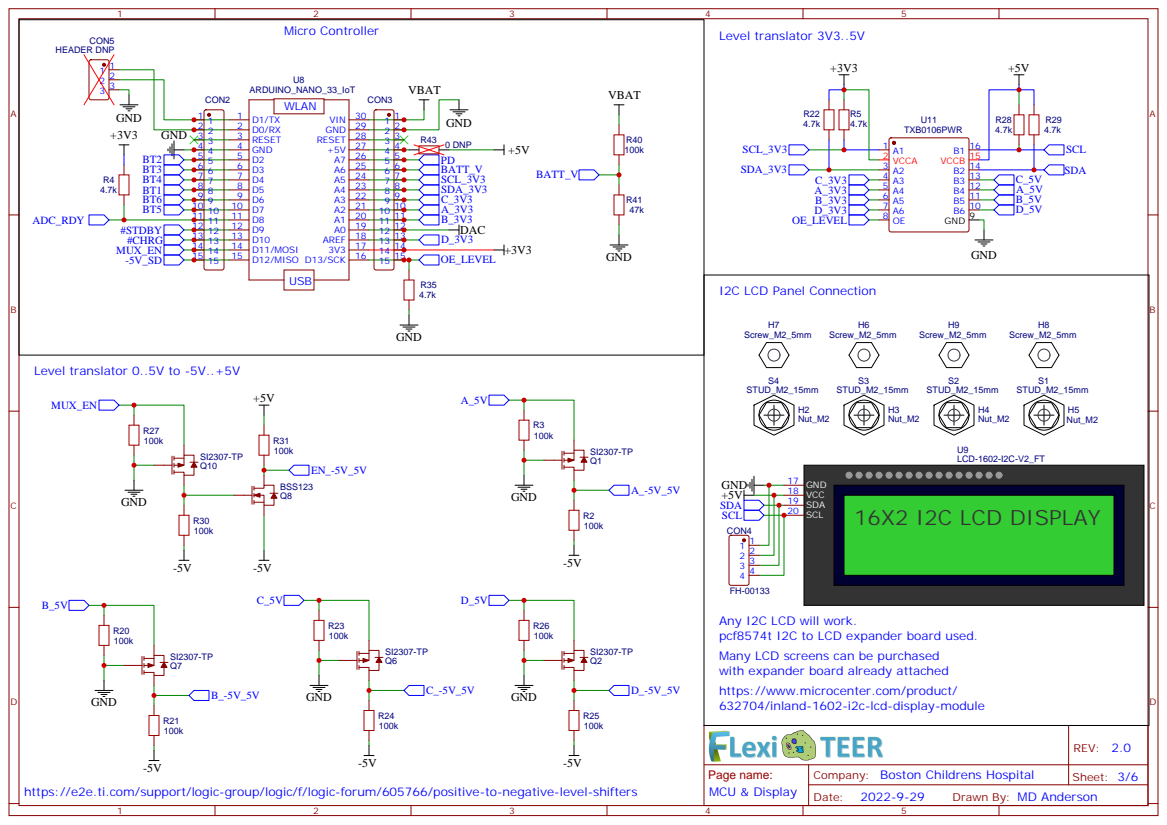
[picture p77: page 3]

Any I2C LCD will work.
pcf8574t I2C to LCD expander board used.
Many LCD screens can be purchased
with expander board already attached
https://www.microcenter.com/product/
632704/inland-1602-i2c-lcd-display-module

Company: Boston Childrens Hospital

https://e2e.ti.com/support/logic-group/logic/f/logic-forum/605766/positive-to-negative-level-shifters

## Voltage Signal Processing

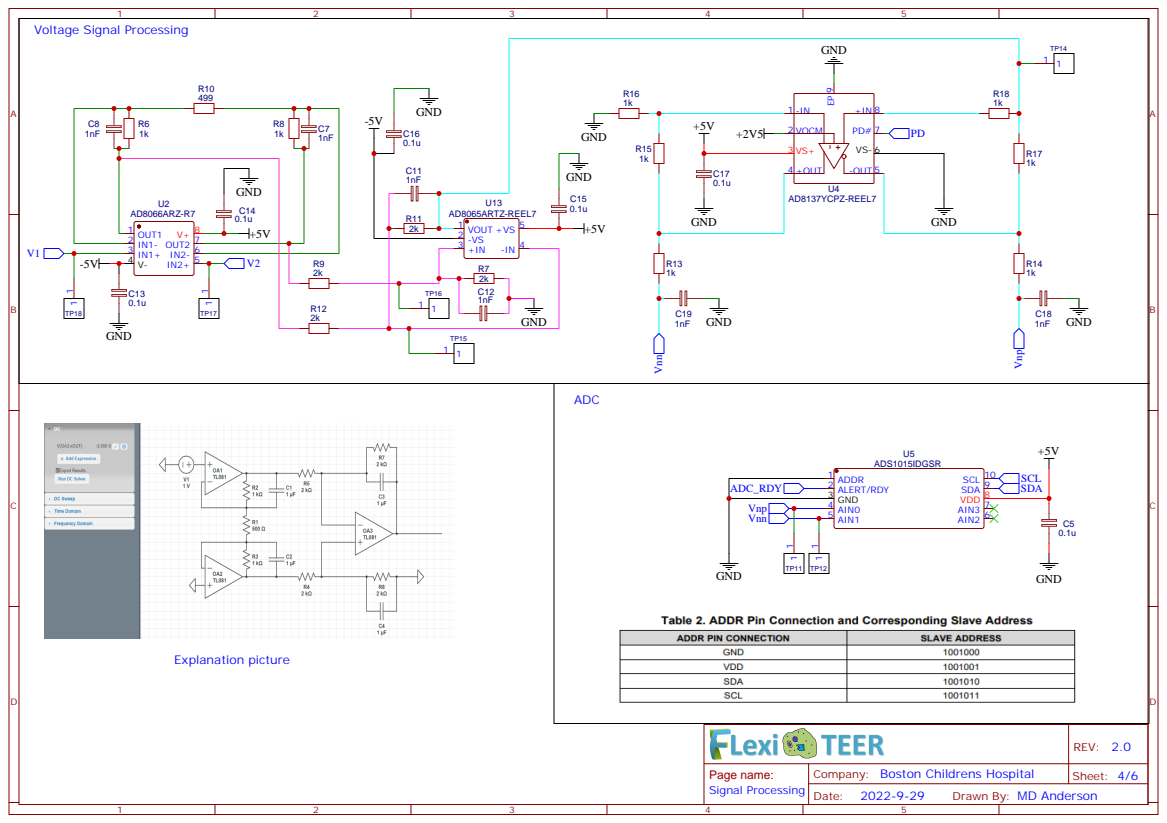
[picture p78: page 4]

Company: Boston Childrens Hospital

## Multiplex I_1 electrode Multiplex electrode


Directly convertable from RJ45 to RJ11
for use on EVOM Meter and vise-versa
Channel 16 (pins 121-128) is reserved for internal calibration of currents via an onboard 1k ohm resistor






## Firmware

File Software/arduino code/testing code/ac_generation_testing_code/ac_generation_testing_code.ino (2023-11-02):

/********PINOUT_DEFINITION*********/
// D0 debug UART RX not used
// D1 debug UART TX not used
#define button_esc 2
#define button_enter 3
#define button_up 4
#define button_right 5
#define button_down 6
#define button_left 7
#define adc_rdy 9
#define batt_stby 9  //charging is done indicator form charger IC
#define batt_chrg 10 //charging is in progress indicator form charger IC
#define mux_enb_pin  11
#define neg_5v_en  12
#define lvl_trans_en_pin 13
// A0 - DAC0
#define b_pin A1
#define a_pin A2
#define c_pin A3
// d_pin connected to AREF
#define sda A4
#define scl A5
#define batt_voltage A6
#define pd_adc_driver_pin A7

/********LIBRARIES*********/

#include <Adafruit_ADS1X15.h>
#include <Adafruit_MCP4725.h>
#include <Arduino.h>
#include <LiquidCrystalIO.h>
#include <IoAbstractionWire.h>
#include <Wire.h>

/********GLOBAL_VARIABLES*********/
int execute = 0;
int buttonState = 0;
int i = -1;
signed int dac_value_bits = 0;
int adc_value_bits = 0;
float dac_value_volts = 0;
float adc_value_volts = 0;
float resistance = 0;
signed int output_current_setpoint = 100;
signed int test_currents[] = {
  100, 50, 10, -10, -50, -100
};  
float   multiplier = 3.00F; 


Adafruit_ADS1015 ads;     /* Use this for the 12-bit version */
Adafruit_MCP4725 dac;
LiquidCrystalI2C_RS_EN(lcd, 0x27, false)


/********INITIAL_CONFIG*********/
void setup() {
  // put your setup code here, to run once:
  Serial.begin(115200);
  delay(2000);
  Serial.println("Hello!");

  pinMode(mux_enb_pin, OUTPUT);
  pinMode(lvl_trans_en_pin, OUTPUT);
  pinMode(a_pin, OUTPUT);
  pinMode(b_pin, OUTPUT);
  pinMode(c_pin, OUTPUT);
  pinMode(DAC0, OUTPUT);
  pinMode(scl, OUTPUT);
  pinMode(sda, OUTPUT);
  pinMode(LED_BUILTIN, OUTPUT);
  pinMode(button_enter, INPUT);
  attachInterrupt(digitalPinToInterrupt(button_enter), onDetectInterrupt, FALLING);

  digitalWrite(lvl_trans_en_pin, HIGH);
  digitalWrite(mux_enb_pin, HIGH);
  digitalWrite(neg_5v_en, HIGH);

  digitalWrite(pd_adc_driver_pin, LOW); // reworked to be the MUX control d
  digitalWrite(a_pin, LOW);
  digitalWrite(b_pin, LOW);
  digitalWrite(c_pin, LOW);
 //                                                                ADS1015  ADS1115
  //                                                                -------  -------
  ads.setGain(GAIN_TWOTHIRDS);  // 2/3x gain +/- 6.144V  1 bit = 3mV      0.1875mV (default)
  // ads.setGain(GAIN_ONE);        // 1x gain   +/- 4.096V  1 bit = 2mV      0.125mV
  // ads.setGain(GAIN_TWO);        // 2x gain   +/- 2.048V  1 bit = 1mV      0.0625mV
  // ads.setGain(GAIN_FOUR);       // 4x gain   +/- 1.024V  1 bit = 0.5mV    0.03125mV
  // ads.setGain(GAIN_EIGHT);      // 8x gain   +/- 0.512V  1 bit = 0.25mV   0.015625mV
  //ads.setGain(GAIN_SIXTEEN);    // 16x gain  +/- 0.256V  1 bit = 0.125mV  0.0078125mV
 
  //#define DAC_RESOLUTION    (10)
  //analogReference(AR_EXTERNAL);
  //analogWrite(DAC0, 426);
  dac.begin(0x60);

  if (!ads.begin()) {
    Serial.println("ADC init .... fail.");
  }
  else{
    Serial.println("ADC init .... success.");
  }

  Wire.begin();
  Serial.println("LCD init.");
  lcd.begin(16, 2);
  lcd.configureBacklightPin(3);
  lcd.backlight();
  lcd.print("click Enter");
  lcd.setCursor(0, 1);
  lcd.print("to start");
}

void onDetectInterrupt()
{
  delay(30);
  if (digitalRead(button_enter) == LOW){
    execute = 2;
  }
  else{
    execute = 1;
  }
  
}

/********MAIN_LOOP*********/
void loop() {
  buttonState = digitalRead(button_enter);
  // put your main code here, to run repeatedly:
  if(buttonState == HIGH){
    digitalWrite(LED_BUILTIN, HIGH);
  }
  else{
    digitalWrite(LED_BUILTIN, LOW);
  }

  if(execute == 1){
    adc_value_bits = -ads.readADC_Differential_0_1();
    adc_value_volts = 100*adc_value_bits*multiplier/5;
    adc_value_volts = adc_value_volts*0.01;
    Serial.print(adc_value_bits);
    Serial.print("bits ");
    Serial.print(adc_value_bits*multiplier);
    Serial.print("mV ");
    Serial.print(adc_value_volts);
    Serial.println("mV");
    resistance = 1000*adc_value_volts/output_current_setpoint;
    Serial.print("R=");
    Serial.print(resistance);
    Serial.println(" Ohm    ");


    lcd.setCursor(0, 1);
    lcd.print("R="); 
    lcd.print(resistance);
    lcd.print(" Ohm    "); 

    delay(200);
  }
  

  if(execute == 2){
    lcd.clear();
    // sizeof(test_currents)/sizeof(test_currents[0]) is used to get an array size use https://www.arduino.cc/reference/en/language/variables/utilities/sizeof/ for reference
    if(i < (sizeof(test_currents)/sizeof(test_currents[0])-1)){
      i = i + 1;
    }
    else{
      i = 0;
    }

    output_current_setpoint = test_currents[i];
    dac_value_bits = (200*output_current_setpoint*0.005/75 + 2.5)*4095 / 5;
    dac_value_volts = 100*dac_value_bits*5/4095;
    dac_value_volts = dac_value_volts*0.01;

    Serial.print("output_current_setpoint = ");
    Serial.println(output_current_setpoint);
    Serial.print("actual output_current_setpoint = ");
    Serial.println(75*(dac_value_volts - 2.5)/200/5000);
    Serial.print("DAC value bits = ");
    Serial.println(dac_value_bits);
    Serial.print("DAC value volts = ");
    Serial.println(dac_value_volts);

    dac.setVoltage(dac_value_bits, false);

    lcd.print("Vd=");
    lcd.print(dac_value_volts);
    lcd.print(" I=");
    lcd.print(output_current_setpoint);
    lcd.print("uA"); 
    execute = 1;
  }
}

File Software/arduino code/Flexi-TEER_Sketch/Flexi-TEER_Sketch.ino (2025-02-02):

/********LIBRARIES*********/

#include "FlexiTeer_pinout.h"
#include <Adafruit_ADS1X15.h>
#include <Adafruit_MCP4725.h>
#include <Arduino.h>
#include <LiquidCrystalIO.h>
#include <IoAbstractionWire.h>
#include <Wire.h>

/********GLOBAL_VARIABLES*********/
bool measure = false;
bool current_increase = false;
bool current_decrease = false;
bool channel_change = false;
bool init_success = false;
float multiplier = 0; //value to multiplier is assigned during ADC init in setup function
byte channel_iterator = B00000;
signed int output_current_setpoint = 20;
float lcd_refresh_time = 2000; //time in ms between data updates for LCD screen
float freq = 12.5; //set frequency in hertz for AC square wave
float switch_time = 1/(freq*2) * 1000; //time between AC flips in ms
unsigned long previousMillis = 0;
unsigned long previousLCDMillis = 0;


signed int pos_dac_value_bits = (output_current_setpoint + 185.64)/0.0907;
float pos_real_current = pos_dac_value_bits * 0.0907 - 185.64; //converts to real current generated
signed int neg_dac_value_bits = (-output_current_setpoint + 185.64)/0.0907;
float neg_real_current = neg_dac_value_bits * 0.0907 - 185.64; //converts to real current generated

int pos_neg_state = 1; //0=negative state, 1=positive state
float resistance = 0;
int resistance_average_count = 0;

Adafruit_ADS1015 ads;     /* Use this for the 12-bit version */
Adafruit_MCP4725 dac;
LiquidCrystalI2C_RS_EN(lcd, 0x27, false)



void setup() {
  Serial.begin(115200);
  while (!Serial) ;
  /********GPIO_CONFIG*********/
  pinMode(mux_enb_pin, OUTPUT);
  pinMode(lvl_trans_en_pin, OUTPUT);
  pinMode(a_pin, OUTPUT);
  pinMode(b_pin, OUTPUT);
  pinMode(c_pin, OUTPUT);
  pinMode(d_pin, OUTPUT);
  //pinMode(neg_5v_en, OUTPUT);
  //pinMode(DAC0, OUTPUT);
  pinMode(scl, OUTPUT);
  pinMode(sda, OUTPUT);
  pinMode(periph_en, OUTPUT);
  pinMode(LED_BUILTIN, OUTPUT);
  pinMode(batt_stby, OUTPUT);
  pinMode(batt_chrg, INPUT);
  pinMode(button_enter, INPUT);
  pinMode(button_esc, INPUT);
  pinMode(button_up, INPUT);
  pinMode(button_right, INPUT);
  pinMode(button_left, INPUT);
  pinMode(button_down, INPUT);

  digitalWrite(batt_stby, HIGH);
  digitalWrite(lvl_trans_en_pin, HIGH);
  digitalWrite(mux_enb_pin, HIGH);
  //digitalWrite(neg_5v_en, HIGH);
  digitalWrite(periph_en, HIGH);

  digitalWrite(a_pin, HIGH);
  digitalWrite(b_pin, LOW);
  digitalWrite(c_pin, LOW);
  digitalWrite(d_pin, LOW);

  /********ADC_CONFIG*********/
 //                                                                ADS1015  ADS1115
 //                                                                 -------  -------
  //ads.setGain(GAIN_TWOTHIRDS);  // 2/3x gain +/- 6.144V  1 bit = 3mV      0.1875mV (default)
  // ads.setGain(GAIN_ONE);        // 1x gain   +/- 4.096V  1 bit = 2mV      0.125mV
  // ads.setGain(GAIN_TWO);        // 2x gain   +/- 2.048V  1 bit = 1mV      0.0625mV
  // ads.setGain(GAIN_FOUR);       // 4x gain   +/- 1.024V  1 bit = 0.5mV    0.03125mV
  // ads.setGain(GAIN_EIGHT);      // 8x gain   +/- 0.512V  1 bit = 0.25mV   0.015625mV
  //ads.setGain(GAIN_SIXTEEN);    // 16x gain  +/- 0.256V  1 bit = 0.125mV  0.0078125mV
  multiplier = 3.00F; 
  Wire.begin();
  delay(1000);
  if (!ads.begin()) {
    Serial.println("ADC init .... fail.");
    init_success = false;
  }
  else{
    Serial.println("ADC init .... success.");
    init_success = true;
  }


  /********BUILT_IN_DAC_CONFIG*********/
  //#define DAC_RESOLUTION    (10)
  //analogReference(AR_EXTERNAL);
  //analogWrite(DAC0, 426);

  /********EXTERNAL_DAC_CONFIG*********/
  dac.begin(0x60);

  /********LCD_CONFIG*********/
  Serial.println("LCD init.");
  lcd.begin(16, 2);
  lcd.configureBacklightPin(3);
  lcd.backlight();
  lcd.print("click Enter");
  lcd.setCursor(0, 1);
  lcd.print("to start");


}


/********MAIN_LOOP*********/
void loop() {

  delay(1);
  unsigned long currentMillis = millis();


  if (currentMillis - previousMillis >= switch_time){
    if (pos_neg_state == 1){
      //record new previous time
      previousMillis = currentMillis;

      //make positive current
      dac.setVoltage(pos_dac_value_bits, false);
      //wait for capacitance to saturate
      delay(switch_time * 0.9);

      // make pos voltage measurement
      int adc_value_bits = ads.readADC_Differential_0_1();
      Serial.println(adc_value_bits);
      float adc_value_volts = 100*(adc_value_bits + 1)*multiplier/5;
      adc_value_volts = adc_value_volts*0.01;
      float resistance_measurement = 1000*adc_value_volts/pos_real_current;
      resistance = ((resistance * resistance_average_count) + resistance_measurement)/(resistance_average_count + 1);
      //add 1 to average count
      resistance_average_count += 1;



      //flip state 
      pos_neg_state = 0;
    }

    else {
      //record new previous time
      previousMillis = currentMillis;

      //make positive current
      dac.setVoltage(neg_dac_value_bits, false);
      //wait for capacitance to saturate
      delay(switch_time * 0.9);

      // make pos voltage measurement
      int adc_value_bits = ads.readADC_Differential_0_1();
      float adc_value_volts = 100*(adc_value_bits + 1)*multiplier/5;
      adc_value_volts = adc_value_volts*0.01;
      float resistance_measurement = 1000*adc_value_volts/neg_real_current;
      resistance = ((resistance * resistance_average_count) + resistance_measurement)/(resistance_average_count + 1);
      //add 1 to average count
      resistance_average_count += 1;

      //flip state 
      pos_neg_state = 1;
    }
}


if (currentMillis - previousLCDMillis >= lcd_refresh_time){
  //update LCD previous time
  previousLCDMillis = currentMillis;

  // update LCD with new resistance info
  lcd.setCursor(0, 1);
  lcd.print("R="); 
  lcd.print(resistance);
  lcd.print(" Ohm    "); 

  lcd.setCursor(0, 0);
  lcd.print("I="); 
  lcd.print(pos_real_current);
  lcd.print(" uA"); 

}
  

  
}

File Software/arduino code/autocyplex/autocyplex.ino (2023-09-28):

/*
 This example connects to an unencrypted WiFi network.
 Then it prints the MAC address of the WiFi module,
 the IP address obtained, and other network details.
 created 13 July 2010
 by dlf (Metodo2 srl)
 modified 31 May 2012
 by Tom Igoe
 */
#include <SPI.h>
#include <WiFiNINA.h>
#include <ArduinoMqttClient.h>





#define SECRET_SSID "raspi-webgui" // your WiFi access point name
#define SECRET_PASS "ChangeMe" // your WiFi password 
///////please enter your sensitive data in the Secret tab/arduino_secrets.h
char ssid[] = SECRET_SSID;        // your network SSID (name)
char pass[] = SECRET_PASS;    // your network password (use for WPA, or use as key for WEP)
int status = WL_IDLE_STATUS;     // the WiFi radio's status


const char broker[] = "10.3.141.1"; // Address of the MQTT server
int        port     = 1883;
const char topic[]  = "control/#";
const char IR1[]  = "readings/IR1";
const char IR2[]  = "readings/IR2";

WiFiClient wifiClient;
MqttClient mqttClient(wifiClient);



#define SLP A7
#define STP A6




int cmd1 = 0;
int cmd2 = 0;
int cmd3 = 0;
int message = 0;
int pump_delay = 2;


void setup() {
  //Initialize serial and wait for port to open:
  Serial.begin(9600);
  //while (!Serial) {
 //   ; // wait for serial port to connect. Needed for native USB port only
  //}

  // attempt to connect to WiFi network:
  Serial.print("Attempting to connect to WPA SSID: ");
  Serial.println(ssid);
  while (WiFi.begin(ssid, pass) != WL_CONNECTED) {
    // failed, retry
    Serial.print(".");
    delay(5000);
  }

  Serial.println("You're connected to the network");
  Serial.println();

  // You can provide a unique client ID, if not set the library uses Arduino-millis()
  // Each client must have a unique client ID
  // mqttClient.setId("clientId");

  // You can provide a username and password for authentication
  // mqttClient.setUsernamePassword("username", "password");

  Serial.print("Attempting to connect to the MQTT broker: ");
  Serial.println(broker);

  if (!mqttClient.connect(broker, port)) {
    Serial.print("MQTT connection failed! Error code = ");
    Serial.println(mqttClient.connectError());

    while (1);
  }

  Serial.println("You're connected to the MQTT broker!");
  Serial.println();

  Serial.print("Subscribing to topic: ");
  Serial.println(topic);
  Serial.println();

  // subscribe to a topic
  mqttClient.subscribe(topic);
  

  // topics can be unsubscribed using:
  // mqttClient.unsubscribe(topic);

  Serial.print("Waiting for messages on topic: ");
  Serial.println(topic);
  Serial.println();


pinMode(A7, OUTPUT);
pinMode(A6, OUTPUT);
pinMode(A5, OUTPUT);
pinMode(2, OUTPUT);
pinMode(3, OUTPUT);
pinMode(4, OUTPUT);
pinMode(5, OUTPUT);
pinMode(6, OUTPUT);
pinMode(7, OUTPUT);
pinMode(8, OUTPUT);
pinMode(9, OUTPUT);
pinMode(10, OUTPUT);
pinMode(11, OUTPUT);
pinMode(12, OUTPUT);
pinMode(13, OUTPUT);

pinMode(A0, INPUT);
pinMode(A2, INPUT);

digitalWrite(A7, LOW);
digitalWrite(A5, LOW);

}


void loop() {
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

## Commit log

2022-04-26 gitbuilding website
    gitbuilding website mostly done. Intro, theory, assembly and modules that can be worked on are ready. BOM needs more details.
    [CustomtranswellTEERchamber.stl, CustomtranswellTEERchamber001.stl, CustomtranswellTEERchamber002.stl, TEErMainDesignA.stl]
2022-04-26 changed gitbuilding workflow location
    changed folder location of gitbuilding CI. Also changed folder name of gitbuilding site to docs and sphinx version to sphinxs_docs
    [CustomtranswellTEERchamber.stl, CustomtranswellTEERchamber001.stl, CustomtranswellTEERchamber002.stl, TEErMainDesignA.stl]
2022-04-26 Deploying to main from @ f4b2710d87d8440a215efbac08c5a8eccf937c25 🚀
    [CustomtranswellTEERchamber.stl, CustomtranswellTEERchamber001.stl, CustomtranswellTEERchamber002.stl, TEErMainDesignA.stl]
2022-04-26 Deploying to main from @ f2aa0beef3d8caa67e53185227a4a9551593a0ad 🚀
    [CustomtranswellTEERchamber.stl, CustomtranswellTEERchamber001.stl, CustomtranswellTEERchamber002.stl, TEErMainDesignA.stl]
2022-04-26 cleaned up
    [CustomtranswellTEERchamber.stl, CustomtranswellTEERchamber001.stl, CustomtranswellTEERchamber002.stl, TEErMainDesignA.stl]
2022-04-26 restore files
    [CustomtranswellTEERchamber.stl, CustomtranswellTEERchamber001.stl, CustomtranswellTEERchamber002.stl, TEErMainDesignA.stl]
2022-04-26 dtry to merge into docs
    [CustomtranswellTEERchamber.stl, CustomtranswellTEERchamber001.stl, CustomtranswellTEERchamber002.stl, TEErMainDesignA.stl]
2022-04-26 Deploying to main from @ 8e69a0aa626ba2ecdce332c5c57523260c742cf2 🚀
    [CustomtranswellTEERchamber.stl, CustomtranswellTEERchamber001.stl, CustomtranswellTEERchamber002.stl, TEErMainDesignA.stl]
2022-04-26 Deploying to main from @ b89f06160fef359f1248ac4d9b3dccece7955216 🚀
    [CustomtranswellTEERchamber.stl, CustomtranswellTEERchamber001.stl, index_BOM.csv]
2022-04-26 Deploying to main from @ f637e81ba58590c746eb9264f819d79bc74541de 🚀
    [CustomtranswellTEERchamber002.stl, TEErMainDesignA.stl, index_BOM.csv]
2022-04-27 undelete files
    strange, all of these files were deleted.
    [CustomtranswellTEERchamber.stl, CustomtranswellTEERchamber001.stl]
2022-04-27 Deploying to main from @ 80ae5aa4ab585714cf01c1672fa94022ce8c49c8 🚀
    [index_BOM.csv]
2022-04-27 updated hardware section
    Updated hardware section of gitbuilding website.
    [CustomtranswellTEERchamber002.stl, TEErMainDesignA.stl]
2022-04-27 Deploying to main from @ 9cb6f5c3cf8e0be75213a12f836dde0e73219b72 🚀
2022-04-27 Website Update
    Updated the assembly, filled out the parts yaml more, silenced fuzzy warnings and fixed issue with Yaml for parts not being read.
2022-04-27 Deploying to main from @ fea5670be3334591f60c9131b8d5f3f3c75ff206 🚀
    [index_BOM.csv]
2022-05-02 gitbuilding folder
    make folder for all gitbuilding material
    [CustomtranswellTEERchamber.stl, CustomtranswellTEERchamber001.stl, CustomtranswellTEERchamber002.stl, TEErMainDesignA.stl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]
2022-05-03 website
    added many sections to website.
    [BOM_PCB_Flexi-TEER_2022-05-02.csv, PickAndPlace_PCB_Flexi-TEER_2022-05-02.csv]
2022-05-10 website repair
    Tried repairing website via recreate gitbuilding site
    [BOM_PCB_Flexi-TEER_2022-05-02.csv, CustomtranswellTEERchamber.stl, CustomtranswellTEERchamber001.stl, CustomtranswellTEERchamber002.stl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]
2022-05-10 move website files
    moved website files to highest level
    [BOM_PCB_Flexi-TEER_2022-05-02.csv, CustomtranswellTEERchamber.stl, CustomtranswellTEERchamber001.stl, CustomtranswellTEERchamber002.stl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]
2022-06-20 Sketch update
    made AD9833 code for fixed freq to test board
2022-09-24 SPICE simulation for AC gen
    [AC_Current generator.kicad_pcb, AC_Current generator.kicad_sch]
2022-10-17 jose comments and battery
    Uploaded jose comments with my commentary. Also, power point on battery charging add ons.
2022-11-16 Create Power Table.xlsx
    Made power table for 5V rail
    [Power Table.xlsx]
2022-11-26 Update Power Table.xlsx
    [Power Table.xlsx]
2023-08-02 Voltage measurment chapter added to bringup report
2023-08-15 Update FlexiTeer_BringUp_report.odt
    updated power connections and added on bilevel converter issue
2023-08-15 Update FlexiTeer_BringUp_report.odt
    added in bilevel converter voltages
2023-08-16 Battery shorting issue discovered
2023-08-18 testing on DAC and MUX
    Finished voltage testing on MUX chips and DAC
    [dac_vs_adc.xlsx]
2023-08-19 Files reorganization. Repository structure change
    [AC_Current generator.kicad_pcb, AC_Current generator.kicad_sch, BOM_Flexi-TEER_2023-03-03.xlsx, BOM_PCB_Flexi-TEER_2022-05-02.csv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]
2023-08-19 BringUp report update
    Visual inspection
    Battery powered chapter added
    [BOM_Flexi-TEER_2023-03-03.xlsx]
2023-08-21 adc driver and volt processing testing
    Completed testing on voltage processing circuit from intsrument to diff amp to ADC driver.
2023-09-01 RJ45 pinout
    [charges.xlsx]
2023-09-09 Update FlexiTeer_BringUp_report.odt
    E15 added. Blocking diode from Arduino VIN to VBAT
2023-09-28 bunch of stuff
    [charges.xlsx, sept_dennis_parts.xlsx]
2023-09-28 docs folder creation for gitbuilding
    [index_BOM.csv]
2023-09-28 Bringup report update. Level shifter
    [BOM_Flexi-TEER_2023-03-03.xlsx]
2023-09-28 Move the webpage related content to the docs folder
    [CustomtranswellTEERchamber.stl, CustomtranswellTEERchamber001.stl, CustomtranswellTEERchamber002.stl, TEErMainDesignA.stl]
2023-10-01 Block diagram updated. BringUp report updated.
    Level shifter investigation finished and concluded.
    AC current generator testing planned
    Inst. amp testing planned
    Overall test plan added
    [Current_gen_calculation.ods]
2023-10-14 External DAC testing
    [Current_gen_calculation.ods]
2023-10-16 files reodered. BringUp report updated
    Supporting documents are put into separate folder.
    Test procedure documented for the AC generator circuit.
    Test plan added for measurements circuits.
    [Current_gen_calculation.ods, dac_vs_adc.xlsx]
2023-10-18 -5V power supply measured and improved
2023-10-28 AC current generator range test
    more test data provided for AC get
    Resistance calculation is added to the software
    [Current_gen_calculation.ods]
2023-11-02 Analog circuits testing finished
    [BOM_Flexi-TEER_2023-03-03.xlsx, Current_gen_calculation.ods]
2023-11-03 bringup report
    marked changes implemented and added in a few comments on changes.
    [CustomtranswellTEERchamber.stl, CustomtranswellTEERchamber001.stl, CustomtranswellTEERchamber002.stl, TEErMainDesignA.stl]
2023-11-06 Power table and bringup report updated
    [Power Table.xlsx]
2023-11-13 Create Multi Transwell TEER sample Plate.pptx
2023-11-29 Block diagram update & Components selection added & extra website pages deleted
    Website files are removed from the root directory, and moved to the docs folder. Most of them had been there already
    [CustomtranswellTEERchamber.stl, CustomtranswellTEERchamber001.stl, CustomtranswellTEERchamber002.stl, TEErMainDesignA.stl]
2024-02-07 Update Multi Transwell TEER sample Plate.pptx
2024-03-21 line item updates
    [charges.xlsx]
2024-04-07 block diagramm update
    [BOM_Flexi-TEER_2023-03-03.xlsx]
2024-09-22 Electronics Rev2.1 released
    [BOM_Flexi-TEER_2024-09-22.csv, PickAndPlace_PCB_Flexi-TEER_2Layers_2024-09-22.csv]
2024-09-26 update 092624
    [FlexiTEER case-transwell Bottom Unit.stl, FlexiTEER case.FCStd]
2024-09-30 order updates
    added line charges prototype 2
    [FlexiTEER case.FCStd, charges.xlsx]
2024-10-01 more case work
    [FlexiTEER case.FCStd]
2024-10-03 model and print update
    updated transwell model and print files
    [FlexiTEER case-transwell Bottom Unit.stl, FlexiTEER case-transwell top.stl, FlexiTEER case.FCStd]
2024-10-07 bio resin pruchase
    [charges.xlsx]
2024-10-10 V2.1 updates
    Made Bring up report for V2.1 and updated Arduino sketch
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2024-10-15 added new program
    started computer triggered flexiteer program
    [DAC_bitvalue_2_current from V2.1 real system.xlsx]
2024-10-22 3d file updates
    [FlexiTEER case-transwell Bottom Unit self seal.stl, FlexiTEER case.FCStd, transwell_self_sealing.FCStd]
2024-10-22 updated model
    [FlexiTEER case.FCStd]
2024-10-24 wiring and 3D model updates
    [FlexiTEER case-transwell triplet bottom unit.stl, FlexiTEER case-transwell triplet top unit.stl, FlexiTEER case.FCStd]
2024-10-28 teer platform updates
    [FlexiTEER case-Base Platform.stl, FlexiTEER case.FCStd, cap_res_breadboard results.xlsx]
2024-11-12 order grant updates
    [charges.xlsx]
2024-11-12 order update
    [charges.xlsx]
2024-11-12 3d model update
    added lid to baseplatform
    [FlexiTEER case-Base Platform.stl, FlexiTEER case.FCStd, baseplatform-lid.stl]
2024-11-13 update case
    [FlexiTEER case.FCStd, baseplatform-lid.stl]
2024-11-27 model updates
    [FlexiTEER case-transwell triplet bottom unit.stl, FlexiTEER case-transwell triplet top unit.stl, FlexiTEER case.FCStd]
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
